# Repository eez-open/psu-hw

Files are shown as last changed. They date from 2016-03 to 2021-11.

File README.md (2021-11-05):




### Ownership and License

The contributors are listed in CONTRIB.TXT. This project uses the TAPR v1.0 license, see LICENSE.TXT.
EEZ _psu-hw_ uses the [C4.1 (Collective Code Construction Contract)](http://rfc.zeromq.org/spec:22) process for contributions.
To report an issue, use the [EEZ psu-hw issue tracker](https://github.com/eez-open/psu-hw/issues).

### Repository structure

Files in this repository are organized using the following folders:

- [Consolidated](https://github.com/eez-open/psu-hw/tree/master/Consolidated) - contains information about all modules. That include **schematics** and **PCB layout** (Eagle, .png, PDF), **BOM** (.ods, PDF) with parts required to build complete dual channel unit (1 x Aux, 2 x Power, and 1 x Arduino Shield).
*Use this as a primary reference for PCB manufacturing and assembling.*
- Aux power - information about Auxiliary power module only
- Power board - information about Power board only
- Arduino shield - information about Arduino Shield only
- [Mechanical](https://github.com/eez-open/psu-hw/tree/master/Mechanical) - drawings for metal custom enclosure and acrylic demonstration enclosure.
- [Building instructions](https://github.com/eez-open/psu-hw/tree/master/Building%20instructions) - details about power supply assembly and wire harness

### Overview

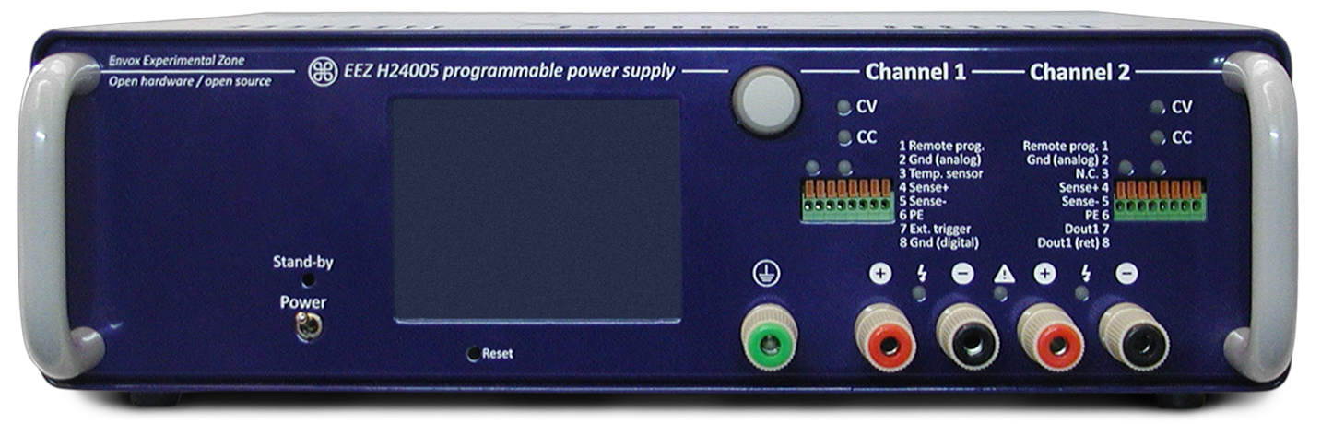
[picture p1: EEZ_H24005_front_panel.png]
prototype


This is repository for the hardware part of the DIY fully programmable dual channel bench power supply. The power supply is designed with taking into consideration the following features and requirements:

- Modular design that allows combining modules with various performance and capability and creation of multiple output solution (min. two channels)
- Voltage regulation (CV), 1/10 mV resolution, up to 50 V (default: 0 - 40 V)
- Current regulation (CC), 0.1/1 mA resolution (multiple ranges, default: 0 - 500 mA / 0 - 5 A)
- Minimal overshoot when new voltage or current level is programmed or in marginal cases such as power on/off
- 15-bit data acquisition resolution
- Various protection mechanisms: over-voltage (OVP), over-current (OCP), over-power (OPP) and over-temperature (OTP), current limiting when temperature sensors or cooling fan fault is detected
- SMPS pre-regulator circuit for lower power dissipation (using e.g. SMPS)
- SMPS pre-regulator's "100% Duty cycle" mode of operation to lower output ripple and noise 
- Switching frequency synchronization if multiple SMPS are utilized
- Output enable (OE) circuit
- Remote voltage sense
- Remote voltage programming
- External digital trigger (3.3 or 5 V logic level)
- Simple AC input protection (surge and transient protection)
- Selectable 115/230 VAC with solid-state (not mechanical!) soft-start/standby circuit
- Simple DC output protection (reverse voltage, over-voltage)
- Serial and parallel connection of the multiple channels
- MCU based digital control module using 32-bit ARM Arduino [Due](https://www.arduino.cc/en/Main/ArduinoBoardDue)
- SPI bus for communication with peripherals
- Galvanic isolation between digital module and power channels
- Real-time clock (RTC) with supercap/batter backup
- EEPROM used as a configuration and calibration parameters storage
- SD-card as an additional storage
- USB support that can be used for remote control, as a debug console and firmware upload
- Ethernet support for remote control
- Local control using TFT touch-screen display
- Incremental encoder with tactile switch as an additional mean of setting output values
- Usage of easy to find components that could be obtain with just single order from suppliers such as Farnell element14, TMU.eu, DigiKey, Mouser, RS online, etc.
- Possibility to house at least dual channel version in affordable and compact (2U height) metallic enclosure
- Comprehensive software support that include [SCPI](https://www.envox.eu/bench-power-supply/psu-scpi-reference-manual/)  remote control, GUI configuration and monitoring and even cross platform (Windows, Linux, OS X) software simulator of the firmware functionality

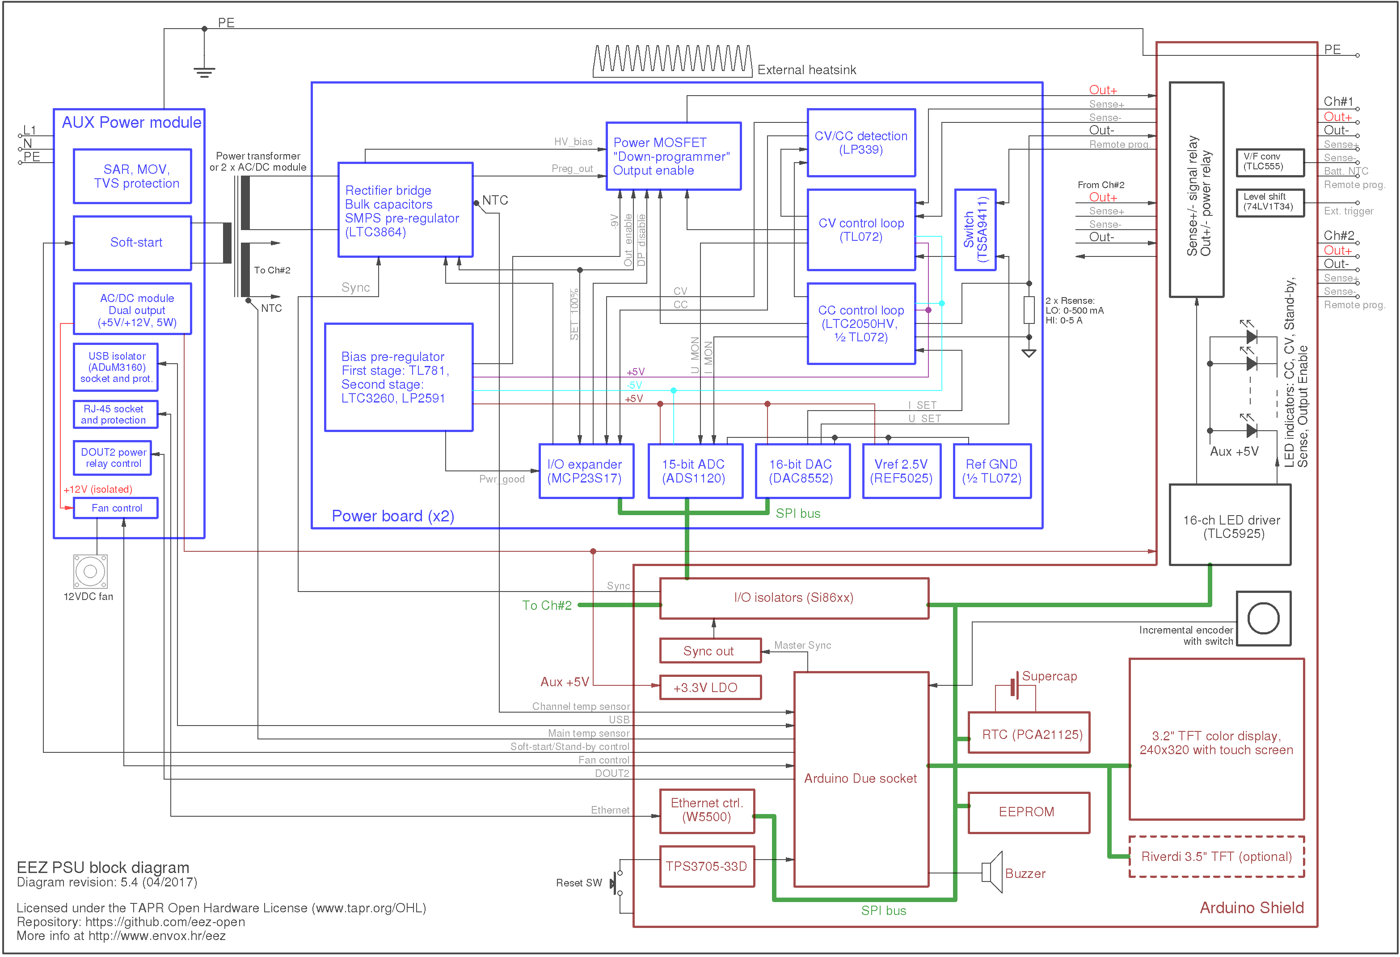
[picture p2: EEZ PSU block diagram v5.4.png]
Programmable dual channel PSU block diagram


**********************

For more information visit https://www.envox.eu/bench-power-supply/introduction/

**********************

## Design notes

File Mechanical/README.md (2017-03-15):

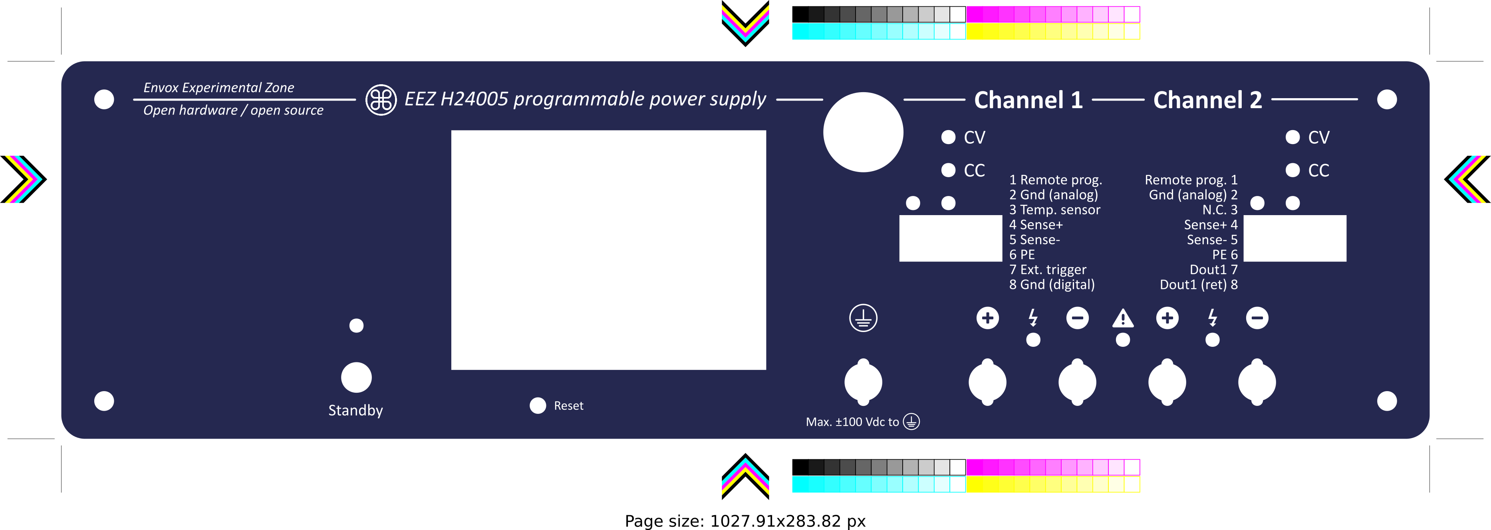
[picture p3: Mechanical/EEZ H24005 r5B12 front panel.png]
front_panel


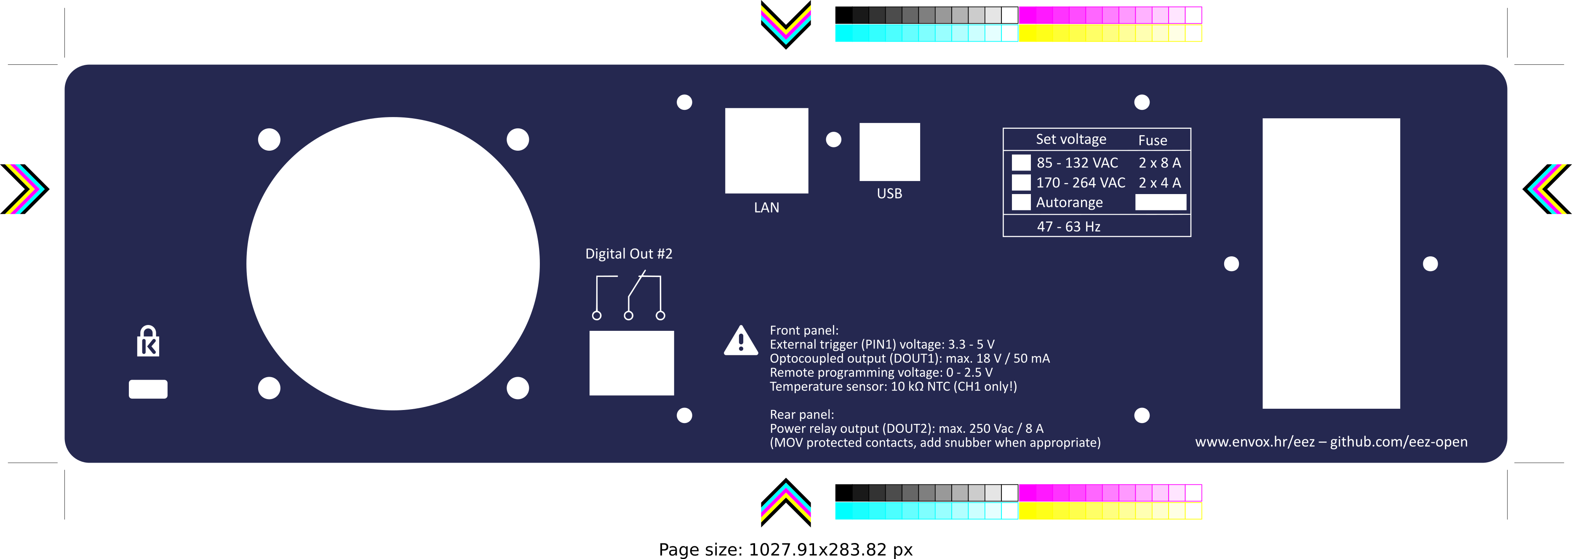
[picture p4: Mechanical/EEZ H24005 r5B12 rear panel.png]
rear_panel


* 3D model generated by [Varisom](http://www.varisom.com)
* Your can use *EEZ PSU H24005 enclosure r5B12 (for 4mm acryl).svg* for laser cut of 4mm thick acryl. The file is prepared for [Formulor](http://www.formulor.de).

**********************

Repository: www.github.com/eez-open
Web site: www.envox.hr/eez

**********************

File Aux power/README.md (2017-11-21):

Please refer to the BOM in [Consolidated/BOM](https://github.com/eez-open/psu-hw/tree/master/Consolidated/BOM) folder where **Board Name** (Col F) is *AUX PS*. Eagle files is available in [Consolidated/Eagle files](https://github.com/eez-open/psu-hw/tree/master/Consolidated/Eagle%20files) folder.

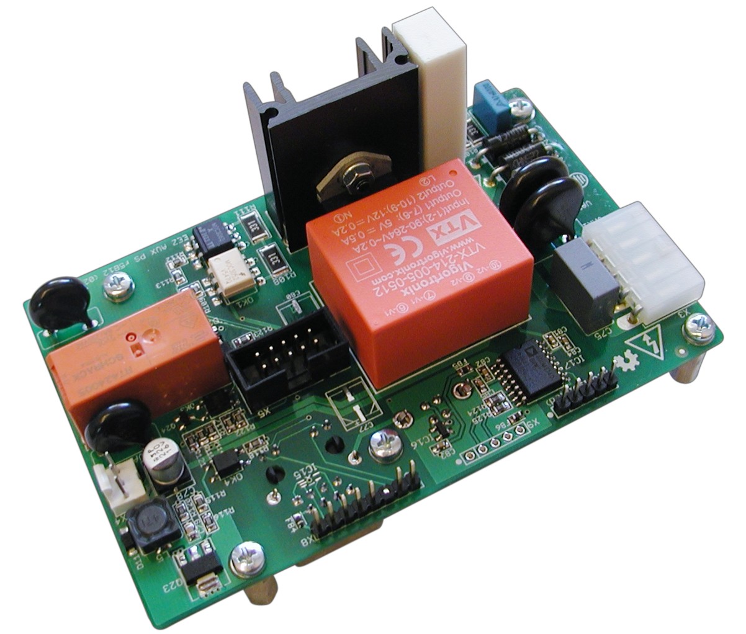
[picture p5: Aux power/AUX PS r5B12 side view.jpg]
EEZ PSU Power board r5B12


**Revision history:**
* 2017-09-24: **r5B13a**
    - USB isolator speed selection ([#56](https://github.com/eez-open/psu-hw/issues/56))
* 2017-03-24: **r5B12a**
    - Fan generates EMI, isolated fan supply, +5 V SMPS replaced with AC/DC module ([#9](https://github.com/eez-open/psu-hw/issues/9))
    - Power relay MCU controlled ([#23](https://github.com/eez-open/psu-hw/issues/23))
    - Ethernet LEDs connected wrong ([#28](https://github.com/eez-open/psu-hw/issues/28))
    - RJ45 modular jack replacement ([#34](https://github.com/eez-open/psu-hw/issues/34))
* 2017-01-11: **r5B11**
    - Added capacitor between ground and Earth ([#17](https://github.com/eez-open/psu-hw/issues/17))
* 2016-10-24: **r5B10**
    - Side 2 of USB isolator (IC19) has now power connected ([#4](https://github.com/eez-open/psu-hw/issues/4))
    - Removed +Vcc (pin 1) on USB header X9 ([#10](https://github.com/eez-open/psu-hw/issues/10))
* 2016-07-24: **r5B9** ([Version 2.0](https://github.com/eez-open/psu-hw/releases/tag/2.0) on github)
	- Replaced PCB iron core transformer with AC/DC module 12 V/5 W that support 115 / 230 VAC power input (bridge rectifier, filter capacitor and 12 V LDO for fan is not needed any more)
	- Changed Ethernet RJ-45 connector model and pinouts (X7)
	- Changed power input connector type (X4)
	- Added triac pull-down resistors R110, R111
	- Optimized number of parts size and values, renumbered reference designators
* 2016-06-14: **r5B8**
    - Master sync and power connector merged into one 10-pin IDC
    - Added place for optional USB isolator ADuM3160
    - Fixed fan control (added C97 and D21)
    - New numbering in sync with consolidated schematics
* 2016-05-26: **r4B43** ([Version 1.0](https://github.com/eez-open/psu-hw/releases/tag/1.0) on github)
	- Correction of swapping pins introduced in r4B40
* 2016-05-01: **r4B42**
    - Changed ramp capacitor from 820p to 1n
    - Fan LDO replaced with MC7812
* 2016-04-06: **r4B41**
    - Add fan control
    - Change power connector
* 2016-01-27: **r4B40**
    - A1 and A2 pins swap on triac Q1 and Q2 to lower required gate current    
    - Change KK1 heatsink type
* 2015-11-14: **r4B39** - *First public release*

**********************

This product is made available under the terms of the TAPR Open Hardware License. See the LICENSE.TXT file that accompanies this distribution for the full text of the license.

**********************

Repository: [www.github.com/eez-open](https://www.github.com/eez-open)  
Web site: [www.envox.hr/eez](https://www.envox.hr/eez)

**********************

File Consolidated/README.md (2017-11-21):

This folder contains consolidated [Eagle](https://github.com/eez-open/psu-hw/tree/master/Consolidated/Eagle%20files) and [Gerber](https://github.com/eez-open/psu-hw/tree/master/Consolidated/Gerber%20files%20%28panel%29) files of all required EEZ PSU modules:
 * Power module **r5B13** (two per unit)
 * Auxiliary power supply **r5B13a**
 * Arduino shield **r5B13a** (digital control)

Centroid files was generated using Eagle's *mount-marks-smd.ulp* script.

All components are renumbered that single BOM can be used. PCB panel is created with four boards to decrease setup fee of PCB manufacturing and assembling.

NOTE: Files for **r5B12** that is used for Crowd Supply crowdfunding campaign can be found [here](https://github.com/eez-open/psu-hw/releases/tag/3.0).

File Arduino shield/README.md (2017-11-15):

Please refer to the BOM in [Consolidated/BOM](https://github.com/eez-open/psu-hw/tree/master/Consolidated/BOM) folder where **Board Name** (Col F) is *Arduino shield*. Eagle files is available in [Consolidated/Eagle files](https://github.com/eez-open/psu-hw/tree/master/Consolidated/Eagle%20files) folder.
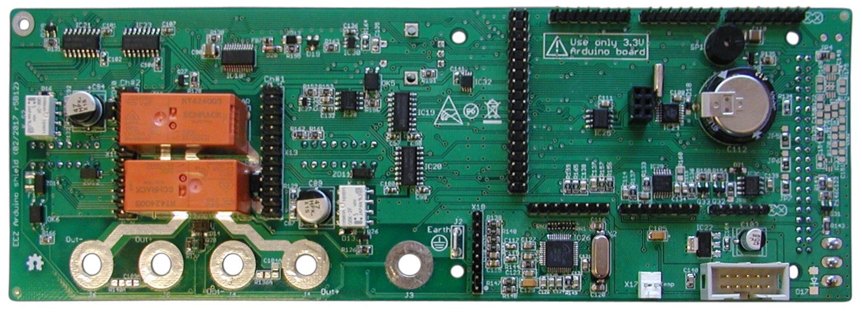
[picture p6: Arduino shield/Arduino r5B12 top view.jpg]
Shield_top

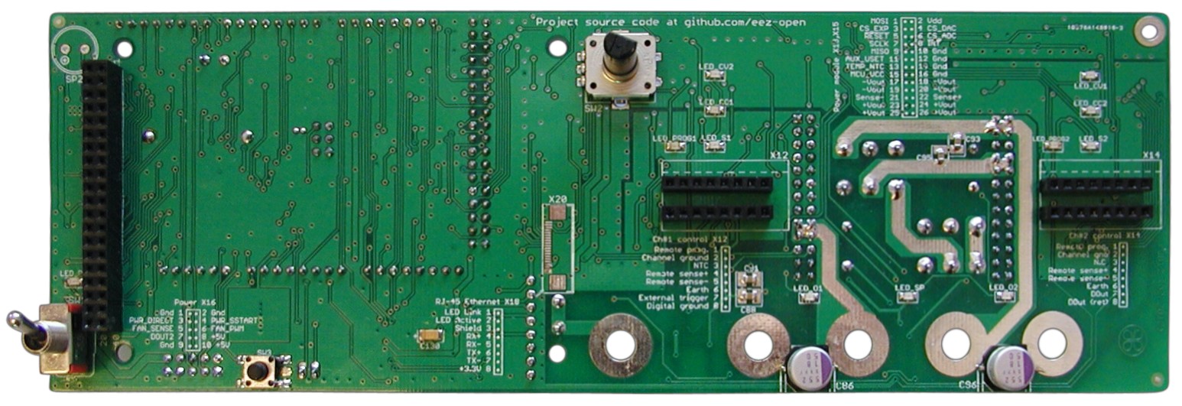
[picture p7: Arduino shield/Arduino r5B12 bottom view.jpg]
Shield_bottom


**Revision history:**
* 2017-11-04: **r5B13a**
    - Soft start and DOUT2 controls ([#36](https://github.com/eez-open/psu-hw/issues/36))
    - Removed JP5, JP6, JP7 ([#59](https://github.com/eez-open/psu-hw/issues/59))
    - R93 PCB layout spacing ([#60](https://github.com/eez-open/psu-hw/issues/60))
* 2017-09-24: **r5B12**
    - X12, X14 connection improvement on PCB ([#43](https://github.com/eez-open/psu-hw/issues/43))
* 2017-02-23: **r5B12**
    - Encoder with switch mounted directly on the PCB ([#20](https://github.com/eez-open/psu-hw/issues/20))
    - Power relay MCU controlled on the AUX PS module([#23](https://github.com/eez-open/psu-hw/issues/23))
    - Support for 3.5" Riverdi TFT touchscreen display ([#24](https://github.com/eez-open/psu-hw/issues/24))
    - Micro SD card socket ([#30](https://github.com/eez-open/psu-hw/issues/30))
* 2017-01-11: **r4B2**
    - +3.3V for buzzer ([#16](https://github.com/eez-open/psu-hw/issues/16))
    - Reorganized capacitors ([#17](https://github.com/eez-open/psu-hw/issues/17))
    - Wrong positions of DOUT pins on X14 push-in connector ([#18](https://github.com/eez-open/psu-hw/issues/18))
* 2016-12-11: **r4B1**
    - Added isolated output on X14 that is replaced with 8 pin push-in connector ([#8](https://github.com/eez-open/psu-hw/issues/8))
    - D33 is added to isolate RESET signal ([#14](https://github.com/eez-open/psu-hw/issues/14))
    - Space for optional R33 is added and IC31 is replaced with 4 AND gate ([#15](https://github.com/eez-open/psu-hw/issues/15))
* 2016-10-24: **r3B5**
    - Small adjustment of TFT display (holes and offset)
    - Removed header for optional WiFi module
    - Ethernet header (X18) is moved to the right ([#5](https://github.com/eez-open/psu-hw/issues/5))
    - Fixed wrong silkscreen for all red LEDs ([#6](https://github.com/eez-open/psu-hw/issues/6))
    - Arduino output is used to generate master sync for switching regulators ([#7](https://github.com/eez-open/psu-hw/issues/7))
    - Additional Cout is added ([#12](https://github.com/eez-open/psu-hw/issues/12))
* 2016-07-23: **r3B4** ([Version 2.0](https://github.com/eez-open/psu-hw/releases/tag/2.0) on github)
	- Corrected WATCHDOG functionality, added possibility to choose between RESET and Power off if MCU stalled
	- Optimized number of parts size and values, renumbered reference designators
* 2016-06-14: **r3B3**
    - Removed suport for Mega2560 - only 3.3 V board such as Due (and hopefully soon [STAR - OTTO](http://www.arduino.org/products/boards/arduino-star-otto) is supported
    - TFT touch screen rotated (landscape view) for housing in more compact (2U height) enclosure. Tested with both SSD1289 and ILI9341 display controllers
    - Reset supervisor and watchdog (TPS3705-33)
    - Power connector replaced with 10-pin IDC to carry master sync out
    - W5500 Ethernet controller
    - 10-pin IDC for channel's SPI bus replaced with 26-pin IDC that carry output power signals, remote sense, remote programming, temperature sensor and SMPS sync
    - Redesigned wiring of output serial/parallel connection
    - Ethernet RJ-45 connector replaced with 8-pin 0.1" header (see also new AUX PS board)
    - 2x5-pin 0.1" header for optional W5500 Ethernet module (eBay)
    - 2x4-pin 0.1" header for optional NRF24L01 Wifi module (eBay)
    - Added support for incremental encoder
    - 4 mm binding posts for remote sensing inputs replaced with 0.1" push-in connector
    - New numbering in sync with consolidated schematics
* 2016-04-06: **r1B14** ([Version 1.0](https://github.com/eez-open/psu-hw/releases/tag/1.0) on github)
    - Added fan control (FAN_PWM, FAN_SENSE)
    - Power connector replaced with 6-pin IDC as on the AUX PS r4B41
    - Removed optional reset connector
* 2016-03-28: **r1B13a**
    - Change remote sense inputs position on X4
* 2016-03-27: **r1B13**
    - Fixed remote sense wiring
    - Output protection redesigned (TVS moved, SAR and MOVs removed)
    - Smaller footprint
    - Remote sense 4 mm banana binding posts replaced with compact "push-in" connectors
    - Digital trigger input (with buffer and level shifter) added
    - THT LEDs replaced with SMD counterparts (lightpipes are now required)
* 2015-12-07: **r1B12b** - *First public release*

**********************

This product is made available under the terms of the TAPR Open Hardware License. See the LICENSE.TXT file that accompanies this distribution for the full text of the license.

**********************

Repository: [www.github.com/eez-open](https://www.github.com/eez-open)  
Web site: [www.envox.hr/eez](https://www.envox.hr/eez)

**********************

Consult [EEZ PSU Arduino pin mapping r5B12.odt
](https://github.com/eez-open/psu-hw/raw/master/Arduino%20shield/EEZ%20PSU%20Arduino%20pin%20mapping%20r5B12.odt) for Arduino pins assignements and [EEZ PSU Arduino shield+BP TLC5925 codes r3B3.odt](https://github.com/eez-open/psu-hw/raw/master/Arduino%20shield/EEZ%20PSU%20Arduino%20shield%2BBP%20TLC5925%20codes%20r3B3.odt) for binding posts connections and LED indications.

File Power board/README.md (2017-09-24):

Please refer to the BOM in [Consolidated/BOM](https://github.com/eez-open/psu-hw/tree/master/Consolidated/BOM) folder where **Board Name** (Col F) is *Power board*. Eagle files is available in [Consolidated/Eagle files](https://github.com/eez-open/psu-hw/tree/master/Consolidated/Eagle%20files) folder.

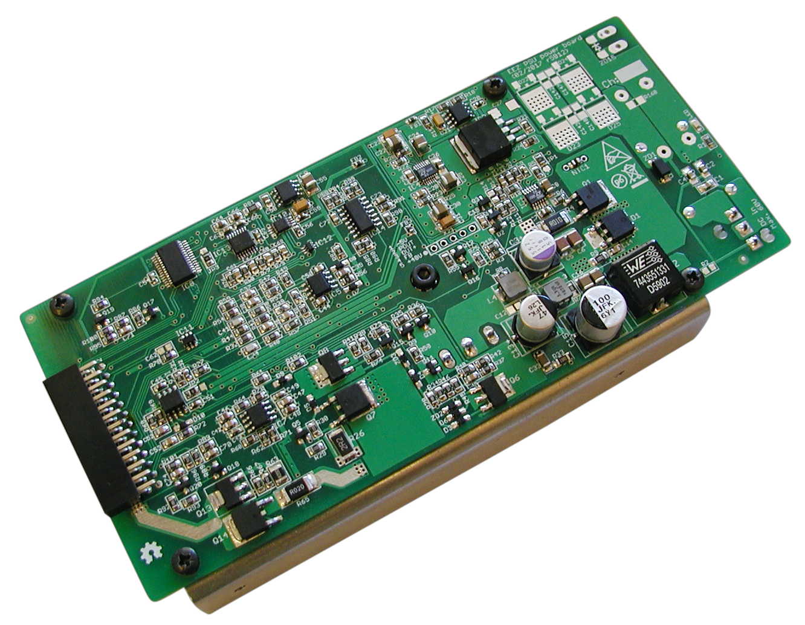
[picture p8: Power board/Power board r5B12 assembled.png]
r5b12


**Revision history:**
* 2017-09-24: **r5B13**
    - High range (0-5 A) sense resistor improvement ([#40](https://github.com/eez-open/psu-hw/issues/40))
    - Additional current range 0-50 mA ([#41](https://github.com/eez-open/psu-hw/issues/41))
    - Output enters unregulated mode too early ([#42](https://github.com/eez-open/psu-hw/issues/42))
    - Remote sense resistors removed ([#44](https://github.com/eez-open/psu-hw/issues/44))
    - Overvoltage protection for V+ output ([#46](https://github.com/eez-open/psu-hw/issues/46))
* 2017-03-11: **r5B12**
    - Dual range current programming and measurement (0-500 mA, 0-5 A)
    - New current monitor (LTC3050HV)
    - 16-bit I/O expander
    - New bias pre-regulator (TL783, LTC3260)
    - Additional Vin capacitor on Power board ([#19](https://github.com/eez-open/psu-hw/issues/19))
    - Rsense with 4-terminal sensing ([#21](https://github.com/eez-open/psu-hw/issues/21))
    - Protection improvement for DC power input ([#25](https://github.com/eez-open/psu-hw/issues/25))
    - PCB is now 15 mm longer (but still compatible with previous heatsink/mounting holes)
* 2016-12-11: **r5B11**
	- Current limiter is removed
* 2016-10-24: **r5B10**
	- Added optional components on the AC power input
	- Voltage programming switch (IC13) wiring is fixed ([#2](https://github.com/eez-open/psu-hw/issues/2))
	- Main heatsink (Q4) earth connection is removed ([#3](https://github.com/eez-open/psu-hw/issues/3))
	- Error amps ground reference offset ([#11](https://github.com/eez-open/psu-hw/issues/11))
* 2016-07-23: **r5B9** ([Version 2.0](https://github.com/eez-open/psu-hw/releases/tag/2.0) on github)
	- DAC Vdd input moved from digital +5 V to analog +5 V power supply
	- Changed power input connector type (X1)
	- Optimized number of parts size and values, renumbered reference designators
* 2016-06-16: **r5B8** - first public release (successor of pre- and post-regulator boards available in [Version 1.0](https://github.com/eez-open/psu-hw/releases/tag/1.0) on GitHub)
	- SMPS pre-regulator based on LTC3864
	- 100% duty-cycle mode of operation for lower output ripple
	- Choice between AC and DC power input
	- Remote output voltage programming
	- Remote sense reverse polarity protection
	- Switching frequency synchronization with other channel via Arduino Shield board (no additional cable is required)
	- On-board SMT temperature sensor (no additional cable is required)

This product is made available under the terms of the TAPR Open Hardware License. See the LICENSE.TXT file that accompanies this distribution for the full text of the license.

**********************

Repository: [www.github.com/eez-open](https://www.github.com/eez-open)  
Web site: [www.envox.hr/eez](https://www.envox.hr/eez)

**********************

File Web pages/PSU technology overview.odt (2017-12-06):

# Technology overview

This programmable bench power supply (PSU) was designed taking into consideration the following mixture of goals and requirements:

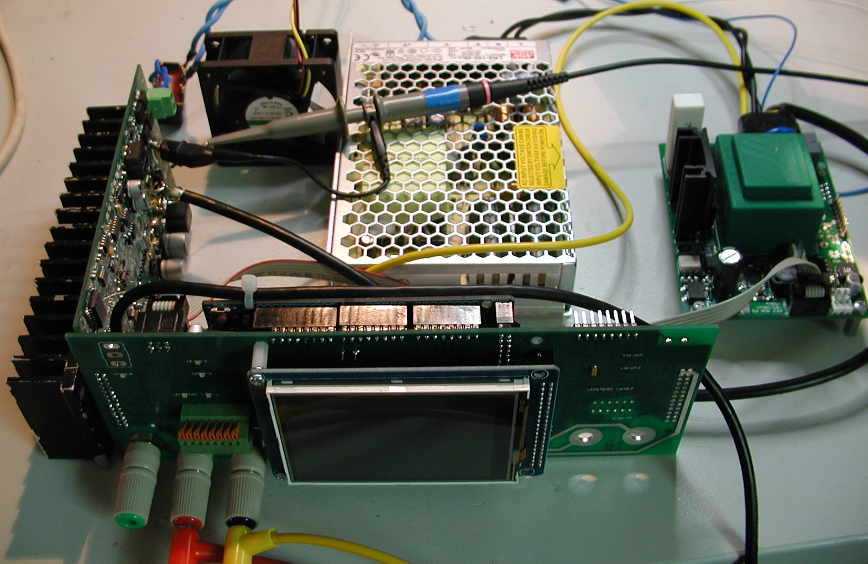
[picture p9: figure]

(http://www.envox.hr/eez/images/eez_psu_prototype_r5b6.jpg)Fig. 1: EEZ PSU early prototype

- Modular design allowing a combination of modules with various performance and capability and creation of multiple output solution (e.g. a minimum of two channels)
- A single input for both internal power and bias supplies, removing any need for a custom multiple secondary winding main transformer
- SMPS (switch mode power supply) pre-regulator circuit for lower power dissipation
- SMPS pre-regulator "100% Duty cycle" operational mode to reduce ripple and noise on the PSU's output
- A TFT color touch-screen as an input control device, and a display output for perfomance information
- Microcontroller (MCU) managed serial and parallel connection for combining PSU channel outputs if suitable
- Voltage limit regulation (CV) with 1/10 mV resolution, up to 50 V (default: 0 – 40 V)
- Current limit regulation (CC) with 0.1/1 mA resolution (when dual range operation, default: 0 – 500 mA / 0 – 5 A)
- Minimal overshoot when a new voltage or current level is programmed, or for cases at the margin, such as power on/off
- A minimum of 15-bit resolution for data acquisition for controlling the PSU
- Multiple protection mechanisms, for both the PSU itself and for devices it powers: over-voltage (OVP), over-current (OCP), over-power (OPP), over-temperature (OTP), and automatic current limiting when faults in temperature sensors or the cooling fan are detected
- Switching frequency synchronization (http://www.powerguru.org/synchronization-of-smps-power-modules/) between switching regulators
- Output enable (OE) circuit, allowing instant (as nearly as possible) output disconnection
- Remote voltage sensing, i.e. Kelvin wiring
- Remote voltage programming (external) “analog” signal control
- External digital trigger signal (3.3 or 5 V logic level)
- Conventional AC input protection for the entire PSU (surge and transient protection)
- Selectable 115/230 VAC with solid-state (not mechanical!) soft-start/standby circuit
- Simple DC output protection (reverse voltage, over-voltage)
- Serial and parallel, firmware controlled, connection of two power output channels
- An MCU based digital control module using 32-bit Arduino/Genuino boards such as the Due (https://www.arduino.cc/en/Main/ArduinoBoardDue)
- An SPI bus (https://en.wikipedia.org/wiki/Serial_Peripheral_Interface_Bus) for peripheral communication
- Galvanic isolation (https://en.wikipedia.org/wiki/Galvanic_isolation) between the digital control circuitry and the power channels
- A real-time clock (RTC) with supercap/battery backup
- An EEPROM for configuration and calibration parameter storage
- Provisions for an SD-card as an additional storage
- USB support for remote control, as a debug console, and for firmware upload
- Ethernet support for remote control
- Fan speed control to reduce operational noise
- An incremental encoder with tactile switch as an additional means of setting output values
- Use of easy to find components readily available from suppliers such as Farnell element14, TMU.eu, DigiKey, Mouser, RS online, etc.
- Possibility to house at least two channels in an affordable and compact (2U height) metallic enclosure
- Comprehensive software support including SCPI remote control, GUI configuration and monitoring, and even a cross platform (Windows, Linux, OS X) PSU function software simulator

Despite the complexity of the proposed design, it should easily possible for DIY assembly needing only intermediate soldering skills for SMD components. The PCB (both Eagle and Gerber files) for PCB production are available on GitHub (https://github.com/eez-open/psu-hw). Arrangements have been made to offer PCBs directly from suppliers, e.g. OSHpark (https://oshpark.com/profiles/eez-open).

Upload of revised firmware will require only novice programming skills and some familiarity with the Arduino IDE. Short video (https://www.youtube.com/watch?v=1iFb0VypKnE) illustrating download and installation of firmware revisons have been made available.

## The PSU building blocks and default configuration

The power supply’s modular design allows freedom to build a flexible, and functional, device. The following modules is possible to use for PSU building:

- Auxiliary power module (http://www.envox.hr/eez/bench-power-supply/psu-auxiliary-supply.html),
- Power board (http://www.envox.hr/eez/bench-power-supply/power-board.html) (one per channel), and
- Arduino Shield (digital control) (http://www.envox.hr/eez/bench-power-supply/psu-digital-control.html)

Each module is described in more detail below. The default configuration has been named EEZ H24005, and will come with the following features:

- Two “floating” channel with programmable output voltage range 0 – 40 V and current 0 – 5 A (max. 155 W per channel) or 0 – 80 V and 0 – 10 A with MCU managed connection in series or parallel
- Remote voltage sensing (with inverse polarity protection), remote voltage programming
- External digital trigger input, external temperature sensor
- Temperature controlled cooling fan
- AC mains power supplied to two AC/DC power modules (48 Vdc, 155 W)
- Arduino Due based digital control
- 3.2” TFT color touch-screen for local console and operating condition display
- Ethernet and USB for remote control (USB is used for firmware update)
- Metal enclosure: 80 (H) x 290 (W) x 240 (D without handles) mm

## Functional block diagram

The block diagram of the PSU is shown below. It includes four modules. The auxiliary power module is used, among other things, for autonomous power of the Arduino Shield board. Complete control of all functionality is performed using the local TFT display touch screen. In addition, the Arduino Shield enables fully featured remote control using serial (via USB) or Ethernet communication.

The remote control is based on a command set that complies with the SCPI (https://en.wikipedia.org/wiki/Standard_Commands_for_Programmable_Instruments) 1999.0 (http://www.ivifoundation.org/specifications/default.aspx) specification which is the de facto standard for middle and high-end commercial power supplies, and many other laboratory instruments.

## Module description


(http://www.envox.hr/eez/images/eez_psu_block_diagram_5_4.png)Fig. 2: EEZ PSU functional block diagram

More information about modules used for building the PSU can be found in the following chapters. A header section with information about module development status has been added to each chapter to simplify progress tracking, like:

Current version | r4B39
Status | Completed, ready for production
PCB manufactured | Yes
PCB assembled | Yes
BOM (https://en.wikipedia.org/wiki/Bill_of_materials) | Yes (Farnell, TME)
File repository | https://github.com/eez-open/psu-hw/tree/master/Aux%20power

## Schematics

{jd_file file==17}

{jd_file file==15}

Revision: 0.2 (of 3) Last modified: 2017-05-10

Revision: 0.2 1 (of 3) Last modified: 2017-05-10

DRAFT – PSU technology overview

Last modified: 2017-05-10 2 (of 3) Doc. version: 0.2

Revision: 0.2 3 (of 3) Last modified: 2017-05-10

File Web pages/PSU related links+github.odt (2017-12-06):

EEZ PSU on the EEVblog forum (http://www.eevblog.com/forum/projects/diy-programmable-dual-channel-bench-psu-0-50v3a/)

EEZ PSU on the DIYaudio forum (http://www.diyaudio.com/forums/equipment-tools/268220-diy-programmable-dual-channel-bench-psu-0-50v-3a.html)

EEZ PSU on the YU3MA.net forum (http://forum.yu3ma.net/showthread.php?tid=980)

EEZ PSU on the Hackaday.io (https://hackaday.io/project/9491-diy-programmable-scpi-bench-power-supply)

EEZ PSU on the Hackster.io (https://www.hackster.io/prasimix/diy-programmable-scpi-bench-power-supply-5e59d5)

Hackaday (https://hackaday.com/2016/02/06/build-yourself-an-awesome-modular-power-supply/) about EEZ PSU (thanks Elliot!)

## DIY power supply projects

We are trying here to make a collection of open source power supplies. Please find below what we found so far (sorted alphabetically) and you are welcome with your suggestions.

Only a project that include some sort of programming and is open source will be listed.

Circuitmaker (http://circuitmaker.com/Projects/F48BC6C2-9005-48B8-87CD-C89CD40F70DC) | Danger From Deer – Bench power supply build (https://dangerfromdeer.com/2016/01/01/bench-power-supply-build-part-1/)
| DIYaudio forum – Frex: Triple outputs 160W Lab PSU – EPSUX3 version 2 (http://www.diyaudio.com/forums/equipment-tools/263471-triple-outputs-160w-lab-psu-epsux3-version-2-a.html)
| EEVblog – μSupply (http://www.eevblog.com/projects/usupply/), a compact Arduino compatible battery powered laboratory power supply
| EEVblog forum – Cowana: Korad KA3003D redesign and upgrade (http://www.eevblog.com/forum/projects/korad-ka3003d-redesign-and-upgrade/)
| EEVblog forum (Leonid Ivanovitch) – PSL-3604 DIY Bench Power Supply (http://www.eevblog.com/forum/projects/diy-bench-power-supply-psl-3604/msg622093/#msg622093)
| Elektor Magazine – Sunil_M: Platino Adjustable Bench Power Supply (https://www.elektormagazine.com/labs/platino-adjustable-bench-power-supply-130406-1)
| Gerrysweeney.com – Fully Programmable Modular Bench Power Supply (http://gerrysweeney.com/fully-programmable-modular-bench-power-supply/)
GitHub (https://github.com/g4lvanix/elbsupply) | Hackaday.io – ElbSupply: Simple linear bench supply (https://hackaday.io/project/4407-elbsupply-simple-linear-bench-supply)
GitHub (https://github.com/fridrikfreyr/DPS201-Hardware) | Hackaday.io – Fridrik: DPS201 Lab PSU (https://hackaday.io/project/1948-dps201-lab-psu)
| Ian Johnston.com – Project #021, Home Built Bench Power Supply (http://www.ianjohnston.com/index.php/projects/57-project-021-home-built-bench-power-supply)
| Kerry Wong – A Digitally Controlled Dual Tracking Power Supply (http://www.kerrywong.com/2013/11/24/a-digitally-controlled-dual-tracking-power-supply-i/)
| Koyodza – Bench lab power supply PSA2 (http://www.koyodza.com/PSA2/index.php?lng=EN)
GitHub (https://github.com/tom-biskupic/LabPSU) | Musings of a WAHZ – Lab Power Supply (http://wahz.blogspot.com.au/p/lab-power-supply.html)
GitHub (https://github.com/qwertyboy/power-supply) | Quertyboy design – Digital PSU (https://qwertyboydesign.wordpress.com/projects-2/digital-psu/)
GitHub (https://github.com/semianalog/mod12003) | Semianalog.com – MOD1 modular power supply (https://github.com/semianalog/mod12003)
GitHub (https://github.com/ThomasVDD/SmartSupply) | ThomasVDD – SmartSupply (http://www.instructables.com/id/Digital-Battery-Operated-Powersupply/) (Digital Battery Operated Power supply)
| Tuxgraphics.org – A Digital DC Power Supply (http://tuxgraphics.org/electronics/201005/bench-power-supply-v3.shtml) (programmable bench power supply unit), hardware version 3.0

## Other

List of open source “ingredients” that could be used as building blocks for DIY power supplies.

GitHub (https://github.com/yu3ma/FSFR2100_LLC_SMPS) | Yu3ma – LLC resonant half-bridge isolated 200W Switched Mode Power Supply based on Fairchild's (now On Semiconductors) FSFR2100XS power controller.
| Iowa Scaled Enginnering – Rebuilding the Elektor 400W power supply: pre-regulator (http://www.iascaled.com/rebuilding-the-elektor-400w-power-supply-pre-regulator/)

DRAFT – PSU related links+github

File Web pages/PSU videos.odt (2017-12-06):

# Videos

<iframe width="320" height="200" src="https://www.youtube.com/embed/jofIdGx2gTg" frameborder="0" allowfullscreen></iframe> | | First preview of the M2 firmware where various input methods are implemented. Thanks to that touch screen become a valid substitute for potentiometer, incremental encoder or numeric keypad. In total five more of operation is possible: Slider (interactive and non-interactive), Step (interactive and non-interactive) and Keypad (non-interactive)
<iframe width="320" height="200" src="https://www.youtube.com/embed/1iFb0VypKnE" frameborder="0" allowfullscreen></iframe> | | The EEZ power supply is using Arduino for programming and monitoring. Therefore its firmware can be partially tested when uploaded on Mega2560 or Due board without having power supply completed. This video contains required steps for upload to the Mega board and test remote control capability based on SCPI commands.
<iframe width="320" height="200" src="https://www.youtube.com/embed/hhGT8GlrUEk" frameborder="0" allowfullscreen></iframe> | | EEZ PSU firmware can be run and evaluate even without having real device on hand. We are developed software simulator that can be run on all major platforms and can be used for presentations but also for development.
<iframe width="320" height="200" src="https://www.youtube.com/embed/b-SwEfrz-Qk" frameborder="0" allowfullscreen></iframe> | | Firmware M2 in addition to the SCPI remote control comes with support for local control via TFT color touchscreen display. This video shows what functionality is covered in this release candidate version.
<iframe width="320" height="200" src="https://www.youtube.com/embed/mfQvZW9PMwk" frameborder="0" allowfullscreen></iframe> | | The EEZ PSU H24005 channel’s output values can be presented in three different ways: Digits Horizontal bar graph Vertical bar graph
<iframe width="320" height="200" src="https://www.youtube.com/embed/s_yasI__Yoo" frameborder="0" allowfullscreen></iframe> | | EEZ PSU H24005 protection mechanisms: Power-on self test Power channel failure Temperature sensor failure Fan failure Over-current protection (OCP) Over-voltage protection (OVP) Over-power protection (OPP) Over-temperature protection (OTP) Remote sense reverse polarity protection
<iframe width="320" height="200" src="https://www.youtube.com/embed/Wbq7mmp_3rc" frameborder="0" allowfullscreen></iframe> | | EEZ PSU H24005 voltage and current calibration using Calibration wizard
<iframe width="320" height="200" src="https://www.youtube.com/embed/wzr1Q3uVOPo" frameborder="0" allowfullscreen></iframe> | | EEZ PSU H24005 remote control using SCPI commands send via serial (USB) or Ethernet. Establishing connection with SCPI controller application (Keysight Connection Expert) is also demonstrated.
<iframe width="320" height="200" src="https://www.youtube.com/embed/5BYZ7RP3CQs" frameborder="0" allowfullscreen></iframe> | | The tracking mode of operation allows one to set output values, states and protections on the both channel by programming just one of them. That could speed up programming and reduce a chance to make mistake when e.g. symmetrical output is needed (on channel is used as positive and another as negative rail) that programmed values is not equal.
<iframe width="320" height="200" src="https://www.youtube.com/embed/Ukn1K1G0pJU" frameborder="0" allowfullscreen></iframe> | | The EEZ H24005 has two isolated channels, the outputs of which can be combined to get higher voltage (up to 80 V) or current (up to 10 A), within the overall power limit of 310 W. Unlike many other power supplies that allow such channel coupling, with the EEZ H24005 you don’t need to pay special attention to wiring thanks to built-in power relays for both voltage and current coupling. This decreases the risk of damaging the power supply due to a tiny wiring mistake.
<iframe width="320" height="200" src="https://www.youtube.com/embed/GRbDXmmBcUA" frameborder="0" allowfullscreen></iframe> | | Presentation of the following system protection mechanisms: Disabling outputs when Auto-recall user profile option is selected Shutdown when any of protection tripped Switching off all outputs when any of protection tripped Disable all outputs on start up
<iframe width="320" height="200" src="https://www.youtube.com/embed/_bRxJo1zC8U" frameborder="0" allowfullscreen></iframe> | | See how to use external analog signal for controlling voltage output.
<iframe width="320" height="200" src="https://www.youtube.com/embed/tPuPrHchPfc" frameborder="0" allowfullscreen></iframe> | | YT mode allows one to directly monitor on the TFT display what is happening over a long period of time with output voltage, current, or power without the assistance of a PC or other external device.
<iframe width="320" height="200" src="https://www.youtube.com/embed/12qwjicYb90" frameborder="0" allowfullscreen></iframe> | | First preview of added incremental encoder that can be used for selecting and setting output values.
<iframe width="320" height="200" src="https://www.youtube.com/embed/1OuaQSNv5TA" frameborder="0" allowfullscreen></iframe> | | Remote voltage sensing can be used to delivery exact voltage to the load regardless of the voltage drop on the connecting cables caused by current flow.
<iframe width="320" height="200" src="https://www.youtube.com/embed/gfUSl8hXwjE" frameborder="0" allowfullscreen></iframe> | | First preview of EEZ Studio, a visual toolkit we developed and used for the EEZ H24005 to create the TFT touch-screen display GUI.
<iframe width="320" height="200" src="https://www.youtube.com/embed/hv_wY3ePyhI" frameborder="0" allowfullscreen></iframe> | | Trigger system and list programming – Part 1 of 2 shows how is possible to trigger a change of output values using one of four trigger sources.
<iframe width="320" height="200" src="https://www.youtube.com/embed/yGn3uoRkYyg" frameborder="0" allowfullscreen></iframe> | | Trigger system and list programming – Part 2 of 2 shows how is possible to program outputs using list of up to 256 different voltage and current values.
<iframe width="320" height="200" src="https://www.youtube.com/embed/wG9moiu5fOY" frameborder="0" allowfullscreen></iframe> | | Using of foot pedal to control outputs.

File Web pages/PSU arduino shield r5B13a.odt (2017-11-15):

# Arduino Shield (digital control)

Current version | r5B13a
Status | Completed, ready for production
PCB manufactured | Yes (r5B12)
PCB assembled | Yes (r5B12)
BOM | Yes (Farnell, TME, Digikey, Mouser, RS)
File repository | https://github.com/eez-open/psu-hw/tree/master/Arduino shield (include Eagle, Gerber and BOM files)
License | TAPR v1.0 (http://www.tapr.org/TAPR_Open_Hardware_License_v1.0.txt)
Contributions | C4.1 (Collective Code Construction Contract) (https://rfc.zeromq.org/spec:22/C4/)

Revision history

2017-11-04: r5B13a

- Improved soft start and DOUT2 controls (#36 (https://github.com/eez-open/psu-hw/issues/36))
- Removed JP5, JP6, JP7 on Arduino shield (#59 (https://github.com/eez-open/psu-hw/issues/59))
- R93 PCB layout spacing (#60 (https://github.com/eez-open/psu-hw/issues/60))

2017-09-24: r5B13

- X12, X14 connection improvement on PCB (#43 (https://github.com/eez-open/psu-hw/issues/43))

2017-02-23: r5B12 (Version 3.0 (https://github.com/eez-open/psu-hw/releases/tag/3.0) on GitHub)

- Encoder with switch mounted directly on the PCB (#20 (https://github.com/eez-open/psu-hw/issues/20))
- MCU controlled power relay on the AUX PS module(#23 (https://github.com/eez-open/psu-hw/issues/23))
- Support for 3.5" Riverdi TFT touchscreen display (#24 (https://github.com/eez-open/psu-hw/issues/24))
- Micro SD card socket (#30 (https://github.com/eez-open/psu-hw/issues/30))

2017-01-11: r4B2

- +3.3V for buzzer (#16 (https://github.com/eez-open/psu-hw/issues/16))
- Reorganized capacitors (#17 (https://github.com/eez-open/psu-hw/issues/17))
- Fixed wrong positions of DOUT pins on X14 push-in connector (#18 (https://github.com/eez-open/psu-hw/issues/18))

2016-12-11: r4B1

- Added isolated output on X14 that is replaced with 8 pin push-in connector (#8 (https://github.com/eez-open/psu-hw/issues/8))
- D33 added to isolate RESET signal (#14 (https://github.com/eez-open/psu-hw/issues/14))
- Space for optional R33 added and IC31 replaced with 4 AND gate (#15 (https://github.com/eez-open/psu-hw/issues/15))

2016-10-24: r3B5

- Small adjustment of TFT display (holes and offset)
- Removed header for optional WiFi module
- Ethernet header (X18) moved to the right (#5 (https://github.com/eez-open/psu-hw/issues/5))
- Fixed wrong silkscreen for all red LEDs (#6 (https://github.com/eez-open/psu-hw/issues/6))
- Arduino output now used to generate master sync for switching regulators (#7 (https://github.com/eez-open/psu-hw/issues/7))
- Additional Cout is added (#12 (https://github.com/eez-open/psu-hw/issues/12))

2016-07-24: r3B4 (Version 2.0 (https://github.com/eez-open/psu-hw/releases/tag/2.0) on GitHub)

- Corrected WATCHDOG functionality, added possibility to choose between RESET and Power off if MCU stalled
- Optimized number of parts size and values, renumbered reference designators

2016-06-14: r3B3

- Removed support for Mega2560 – only 3.3 V board such as Due (and hopefully soon STAR - OTTO (http://www.arduino.org/products/boards/arduino-star-otto)) now supported
- TFT touch screen rotated (landscape view) for housing in more compact (2U height) enclosure. Tested with both SSD1289 and ILI9341 display controllers
- Reset supervisor and watchdog (TPS3705-33)
- Power connector replaced with 10-pin IDC to carry master sync out
- W5500 Ethernet controller
- 10-pin IDC for channel's SPI bus replaced with 26-pin IDC which carries output power signals, remote sense, remote programming, temperature sensor and SMPS sync
- Redesigned wiring of output serial/parallel connection
- Ethernet RJ-45 connector replaced with 8-pin 0.1" header (see also new AUX PS board)
- 2x5-pin 0.1" header for optional W5500 Ethernet module (eBay, etc.)
- 2x4-pin 0.1" header for optional NRF24L01 WiFi module (eBay, etc.)
- Added support for incremental encoder
- 4 mm binding posts for remote sensing inputs replaced with 0.1" push-in connector

2016-04-06 r1B14 (Version 1.0 (https://github.com/eez-open/psu-hw/releases/tag/1.0) on github)

- Added fan control (FAN_PWM, FAN_SENSE)
- Power connector replaced with 6-pin IDC as on the AUX PS r4B41
- Removed optional reset connector

2016-03-28 r1B13a

- Changed remote sense inputs position on X4

2016-03-27 r1B13

- Fixed remote sense wiring
- Output protection redesigned (TVS moved, SAR and MOVs removed)
- Smaller footprint
- Remote sense 4 mm banana binding posts replaced with compact "push-in" connectors
- Digital trigger input (with buffer and level shifter) added
- THT LEDs replaced with SMD counterparts (lightpipes now required)

2015-12-07 r1B12b – First public release


(http://www.envox.hr/eez/images/arduino_shield_r5b12_top.jpg)Fig. 1: Arduino Shield assembled (PCB r5B12, top side)


(http://www.envox.hr/eez/images/arduino_shield_r5b12_bottom.jpg)Fig. 2: Arduino Shield assembled (PCB r5B12, bottom side)

The Arduino Shield (https://www.arduino.cc/en/Main/ArduinoShields) has three important functions:

- Carrying power output binding posts and remote sense inputs with the option to connect two output channels in series or parallel,
- MCU programming and supervision of up to two Power boards (http://www.envox.hr/eez/bench-power-supply/power-board.html) and
- Local user interface using TFT color touch-screen display

Additionally it offers the following functionality:

- Multiple LED status and operational indications
- Soft-start/Stand-by control (hosted on Auxiliary power (http://www.envox.hr/eez/bench-power-supply/psu-auxiliary-supply.html) module)
- MCU fan control (hosted on Auxiliary power (http://www.envox.hr/eez/bench-power-supply/psu-auxiliary-supply.html) module)
- EEPROM storage
- Real-time clock (RTC) with supercap (https://en.wikipedia.org/wiki/Supercapacitor) back-up
- Reset supervisor with watchdog
- Beeper
- Analog inputs for temperature readings
- Ethernet communication
- Incremental encoder with switch
- Switching regulator frequency synchronization
- External digital trigger
- Power relay (DOUT2) control (hosted on Auxiliary power (http://www.envox.hr/eez/bench-power-supply/psu-auxiliary-supply.html) module)
- Optional audio amplifier and 20-pin FFC connector for 3.5” Riverdi TFT touch-screen displays

## Binding posts section

This section has been added to simplify wiring of power binding posts, remote sense inputs, and serial and parallel connection control for the two channels without external wiring changes. Wiring of power outputs is controlled by the MCU firmware to reduce the possibility of an operator error, such as:

- channel output voltages and currents are not adjusted properly before connecting them in parallel,
- channel output polarities are mismatched or
- serial wiring is established while outputs are enabled that increase the risk of electric shock because of touching output when 50 V or more is present. An exceptionally dangerous situation since fire or electrocution is much increased at these voltages.

Output terminals have been located on the PCB so that direct mounting of 4 mm paired binding posts (with standard spacing of 19.05 mm / 750 mils) is supported. Power outputs are protected against reverse polarity and over-voltage spikes using TVS (ZD7, ZD10). Output capacitors (C87+R129, C89 and C92+R132, C94) required for both stable operation and lowered output PARD (http://power-topics.blogspot.hr/2008/11/ripple-noise-specs-and-measurements.html) (ripple and noise) of Power modules are also mounted on the Power board PCB. For additional attenuation of PARD, C86 and C96 (elco-polymer, like OS-CON) are mounted in close proximity to the power output binding posts.

Connecting two power outputs in series or parallel is done with two 8 A relays (K_SER, K_PAR). The channel outputs are separated/isolated when both relays are inactive; J1, J4 and J5, J6 binding post pairs are used for Ch1 and Ch2 respectively. When operating in either series or parallel, only two central binding posts (J4, J5) are used. This design choice was intentional to decrease the chance of bringing high voltage or current to loads already connected to either channel. In this way, the user need to physically move one or another wire to make a new operational scheme effective.

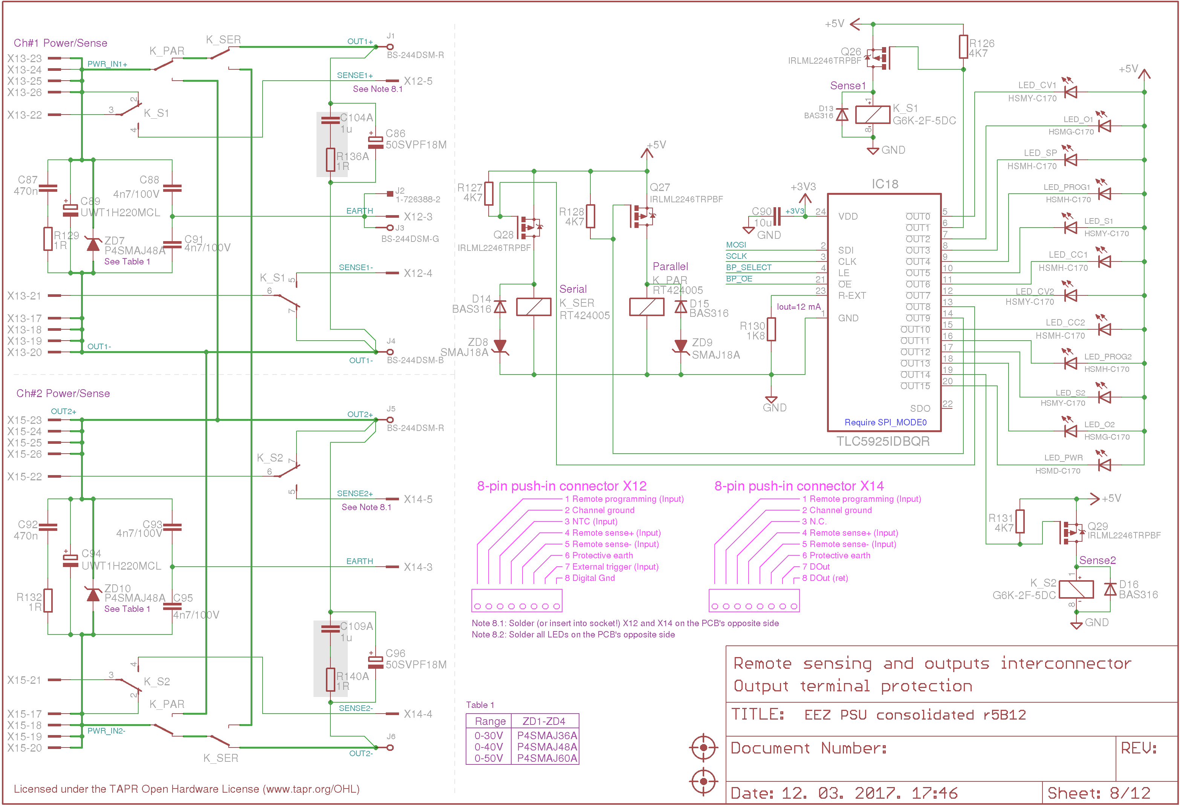
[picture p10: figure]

(http://www.envox.hr/eez/images/arduino_shield_r5b12_sheet8of12.png)Fig. 3: Binding post section, relays and LED driver

In addition, with this scheme with K_SER and K_PAR avoids the possibility of Power board damage due to a firmware bug that can activate both modes concurrently. The wiring in Fig. 4 makes clear that Parallel mode is more “significant” – when it’s selected it locks out the K_SER input contacts.

An obvious drawback of this wiring approach is disconnecting the C86, C96 capacitors when power outputs are coupled. Therefore, if lower PARD figure is still needed an external capacitor may be necessary.

When driving the serial or parallel relays, the following things have to be taken into consideration:

- Voltage and current must be zero before the channels are connected or disconnected. The easiest way to do that is to disable output (OE is off) but it's also recommended to also program output values to zero.
- Coupling outputs in parallel is safely possible if programmed output voltages are the same on both channels
- Optionally, the down-programmer circuit could be disconnected on one of the channels when coupling in parallel is selected

Of course, wiring of two channels can be done independently of their built-in functionality. In this case, the recommendations above still apply.

Channel outputs, by default, are “floating” with regard to the PSU earth potential provided via a separate 4 mm binding post J3. This permits either negative or positive output to an external earth potential.

Note that with positive output connected to the Earth you should never take measurements with earth referenced instruments such as an oscilloscope. That will create a short circuit and excessive output current could damage the connected instrument’s wiring.

Remote sense is performed with signal relays (K_S1, K_S2), and local sensing is selected when they are not active. Activation of remote sensing is indicated with an LED (LED_S1, LED_S2); two additional wires (or perhaps a 2-wire shielded cable) has to be used to connect sensing inputs to the load. This technique is called Kelvin wiring and is common in high precision electronics work. Caution is required to avoid polarity mismatches. But, even if a polarity mismatch happens, a reverse polarity detection (http://www.envox.hr/eez/bench-power-supply/power-board.html#reverse_polarity) circuit on each Power board will limit output voltage, and an alarm for the MCU will be triggered.

All relays are indirectly driven (Q26-Q29) by a TLC5925 (http://www.ti.com/product/tlc5925) (IC18) which is a 16-channel constant current LED driver. A multiple output LED driver device was chosen because there are 12 LEDs used to indicate various condition during PSU operations:

- Power output is enabled (LED_O1, LED_O2, green, positioned between positive and negative binding posts on each channel)
- Power outputs are coupled in series (or parallel) (LED_SP, red, positioned between Ch1 negative, and Ch2 positive binding posts)
- CC limit mode (LED_CC1, LED_CC2, red, above push-in connector)
- CV limit mode (LED_CV1, LED_CV2, yellow, above CC LED)
- Remote sense is enabled (LED_S1, LED_S2, yellow, above the remote sense input pins of the push-in connector)
- Remote programming is enabled (LED_PROG1, LED_PROG2, red, above the remote sense input pins of the push-in connector) and
- Standby mode (LED_PWR, orange, between reset and the power switch)

All allowable binding posts connections with LED indications and programming codes that can be used for controlling the TLC5925 can be found here (http://www.envox.hr/eez/bench-power-supply/psu-digital-control/psu-binding-posts-section-programming-codes.html). Please note that the TLC5925 is powered with 3.3 V while all connected loads (LEDs and relays) use 5 V. This is not an issue for powering the LEDs because the TLC5925 outputs are constant current (max. current is defined with R130 or ~12.1 mA for 1.8 KΩ).

## Arduino board

The Arduino Shield can work with any 3.3 V Arduino board. Currently, that means only one – the Arduino Due (two :)) which is a 32-bit ARM Cortex-M3 (https://en.wikipedia.org/wiki/ARM_Cortex-M3) based board that comes in “Mega” form-factor. Hopefully more boards with the same form-factor will be available in the future from various Arduino designers (e.g. .org STAR – OTTO (http://http://www.arduino.org/products/boards/arduino-star-otto)) or other sources. Connection with the Arduino board requires 8 connectors (Fig. 8): ICSP, DIGITAL, PWML, PWMH, ADCL, ADCH, COMM and POWER. They are located at the three board sides (with ICSP somewhere in the middle!); we learned that this arrangement is rather impractical when the board must be removed. Close attention is required to avoid bending one or more pins on the Arduino Shield side.

Controlling two channels and all peripherals used 64 I/O pins (http://www.envox.hr/eez/bench-power-supply/psu-digital-control/psu-arduino-shield-pin-mapping.html) (SPI (https://en.wikipedia.org/wiki/Serial_Peripheral_Interface_Bus) lines on ICSP connector were not counted) leaving “only” six pins available for future upgrades. Most of them (26) are assigned to the TFT LCD with its touch-screen display. Using another display with high speed serial interface can potentially reduce that to only 2 or 3 pins (+ SPI). An optional 20-pin FFC connector (X20) for 3.5” Riverdi TFT touch-screen displays is already available on the PCB as a possible migration path to a new more efficient local display solution.

Perhaps it’s worth mentioning that each additional Power board requires only four dedicated I/O pin for control. With existing pin mapping that give room for one additional channel (of course that will also require a new PCB layout). The newly introduced 16-bit I/O expander on the Power board (r5B12) could reduce this to only two I/O pin (+ SPI that is currently shared between all peripherals). The pin mapping of all used pins is described here (http://www.envox.hr/eez/bench-power-supply/psu-digital-control/psu-arduino-shield-pin-mapping.html).

Input power of the Arduino Shield is +5 V, supplied by X16 from the Auxiliary power (http://www.envox.hr/eez/bench-power-supply/psu-auxiliary-supply.html) module. The Arduino Due is a 3.3 V board, but 5 V is used as its power input. It can be powered via the POWER header 5V pin (or from a USB port). An internal 3.3 V LDO regulator is used to adjust the 5 V to 3.3 V for local on board use. That LDO is not used for powering 3.3 V circuits on the Arduino Shield. An additional regulator is used for that purpose (IC22).

## Digital isolators

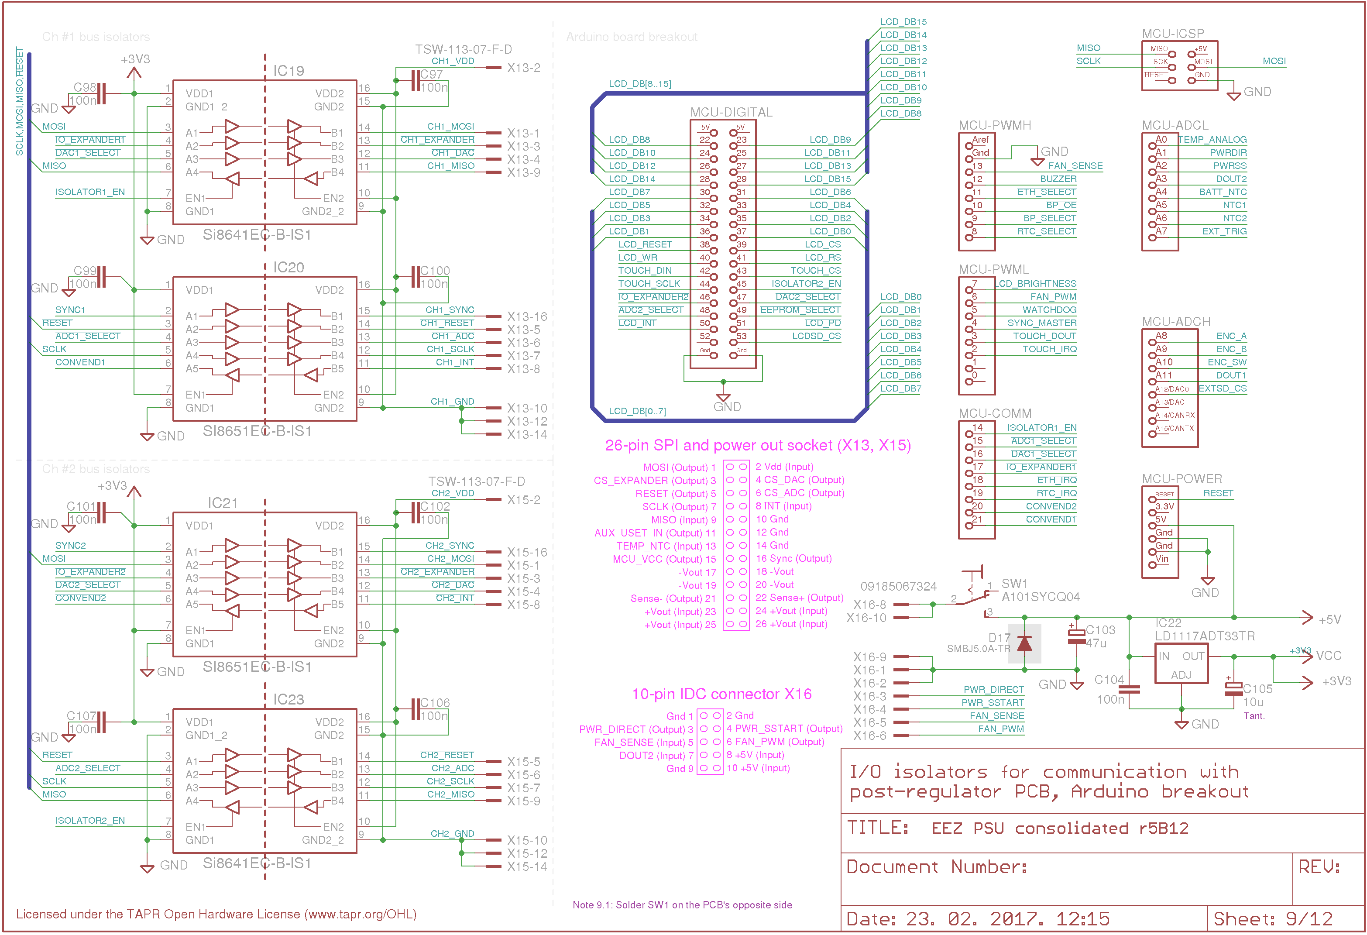
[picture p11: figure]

(http://www.envox.hr/eez/images/arduino_shield_r5b12_sheet9of12.png)Fig. 4: Digital isolators, 3.3V LDO and Arduino board connections

The Arduino Shield can control two PSU channels which are electrically isolated by default; they must remain isolated when they are connected to the Shield. That means digital control signals cannot share the common ground. If such a connection occurs (perhaps via an accidental short), it could be even dangerous when, for instance, channel outputs are connected in serial or when the PSU is used as a dual rail source (positive output from one channel is connected to the another channel's negative output). Digital channel isolation is accomplished using high speed Si86xx series (https://www.silabs.com/products/power/isolators/Pages/Si86xx-Digital-Isolators.aspx) digital isolators.

Two digital isolators are used per channel to isolate 7 outputs and 2 inputs (IC19, IC20 for Ch1 and IC21, IC23 for Ch2). They are SPI lines, chip selects for SPI peripherals on the Power board (ADC, DAC and I/O expander), and Master sync for switching regulators frequency synchronization. The MISO line (Master-in-Slave-out) SPI line requires additional control (ISOLATOR1_EN, ISOLATOR2_EN outputs) to select receiving of data from one channel at a time. Otherwise, data corruption will be inevitable.

## Power board I/O connector

Two 26-pin headers (X13, X15) are used to connect with the Power boards. Functions of the first ten pins follows the ICSP (https://en.wikipedia.org/wiki/In-system_programming) 10-pin header mapping carrying digital signals for SPI, chip selects and supply voltage for the channel side (B side in accordance to Silicon Labs datasheet) of the digital isolators. The rest of the connector is used for various analog signal and power lines as described in table below.

# | I/O name | Active | Description

1 | MOSI | High | MOSI (SPI)
2 | Vdd | Power | Power board +5 V output
3 | CS_EXPANDER | Low | I/O expander chip select
4 | CS_DAC | Low | DAC chip select
5 | RESET | Low | Reset
6 | CS_ADC | Low | ADC chip select
7 | SCLK | High | SCLK (SPI)
8 | INT | Low | I/O expander IRQ (https://en.wikipedia.org/wiki/Interrupt_request_(PC_architecture)) / ADC conversion end
9 | MISO | High | MISO (SPI)
10 | Gnd | Power | Power board ground
11 | AUX_USET_IN | Analog | Remote voltage programming
12 | Gnd | Power | Power board ground
13 | TEMP_NTC | Analog | Power board temperature sensor (NTC)
14 | Gnd | Power | Power board ground
15 | MCU_VCC | Power | Arduino board +3.3 V output
16 | Sync | High | Master sync for switching regulator’s frequency synchronizations
17 | Vout- | Power | Negative power output
18 | Vout- | Power | Negative power output
19 | Vout- | Power | Negative power output
20 | Vout- | Power | Negative power output
21 | Sense- | Analog | Remote voltage sensing negative signal
22 | Sense+ | Analog | Remote voltage sensing positive signal
23 | Vout+ | Power | Positive power output
24 | Vout+ | Power | Positive power output
25 | Vout+ | Power | Positive power output
26 | Vout+ | Power | Positive power output

## I/O peripherals

SPI peripherals might be added to the Arduino Shield (Fig. 8) to provide functions are not regularly available on the Arduino board. In fact, for the Arduino Due that is partially true because its MCU has RTC (Real-time-clock), and even Ethernet. But as far as we know, the former cannot be easily powered from a back-up source when the main power is switched off, and the latter is not exposed to an external connector nor supported through Arduino libraries. The on-board RTC (IC24) supply is backed up with 1 F Supercap (C112) which should be enough for keeping it running for a couple of weeks when the main power is not present.

Ethernet communication is accomplished using (IC26). In addition, an EEPROM (IC25) is added since MCU on Arduino Due does not have any EEPROM memory.

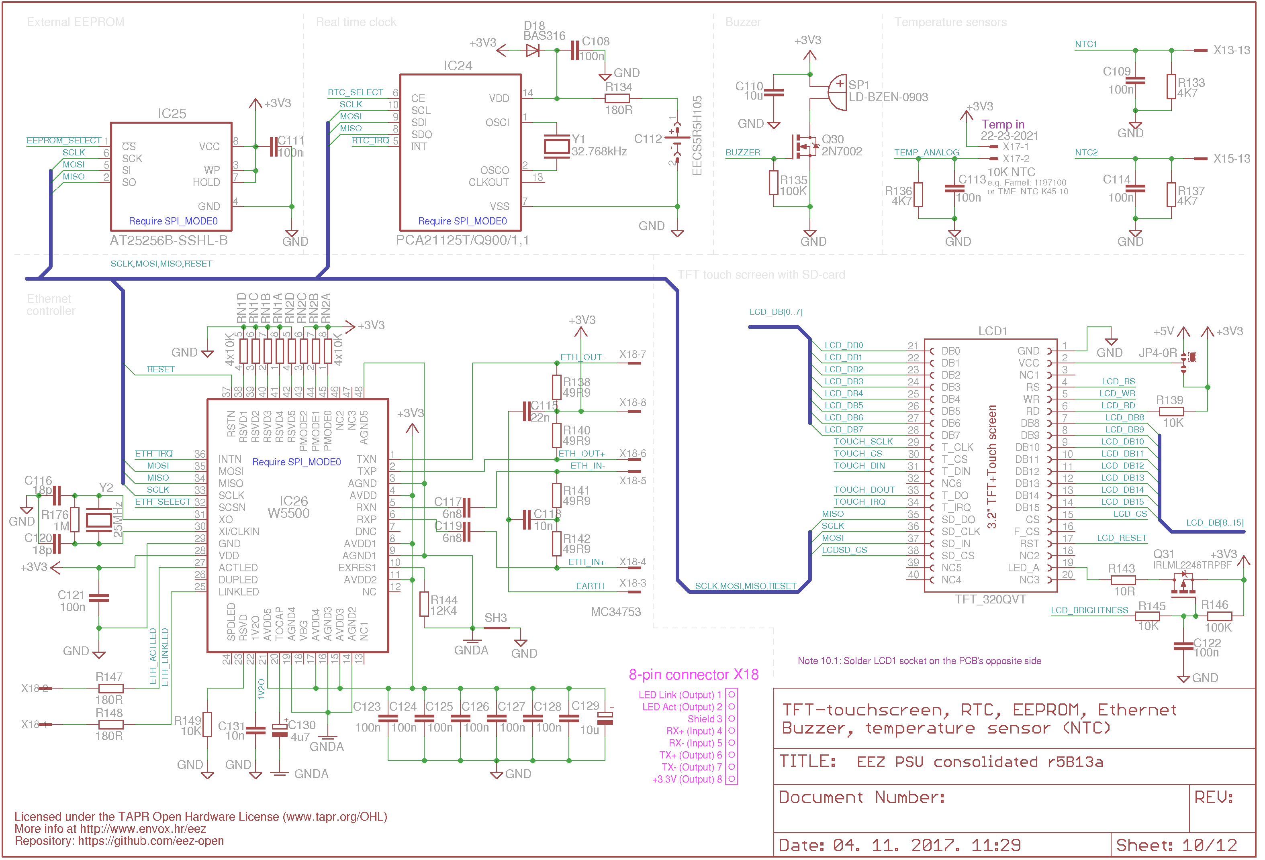
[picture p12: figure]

(http://www.envox.hr/eez/images/arduino_shield_r5b13a_sheet10of12.png)Fig. 5: Arduino Shield peripherals

The TFT display (Fig. 6) has 3.2” diagonal size, 262K (18-bit) colors and 240 x 320 pixels (rotated horizontally!) that gives enough room to display much important information about both channels and system status and messages simultaneously. Color coding could improve the visibility of one or another value amongst the data from various sources. This display unfortunately is not available yet through major suppliers mentioned in the BOM (https://github.com/eez-open/psu-hw/tree/master/Consolidated/BOM), but it can be easily found on any major on-line shopping site (eBay, AliExpress, etc.) by searching for TFT_320QVT. Additionally, the search query could be further narrowed by physical size (3.2 Inch), resolution (240 x 320), and the name of the matching LCD controller (SSD1289 (http://www.solomon-systech.com/en/product/display-ic/smart-tft-lcd-driver-controller/ssd1289/)). The newer display version comes with a new LCD controller (ILI9341); the PSU firmware supports both versions.

This display also comes with SD card slot that can be used as mass storage for such things as data logging, user’s programs, data, etc.

A few words about selection of SPI bus. It’s very common for devices with similar functionality and complexity as the EEZ PSU to use an I²C bus for communication with various peripherals. Devices with such interfaces are in general cheaper, require only two lines for communications (no SCLK and no dedicated chip select for each device is required!), and are well supported with software libraries. I²C can be very beneficial for low end MCUs with low I/O pin count. But that also in general means less processing power and memory which makes them unsuitable for the firmware complexity we need. We have already mentioned that the Arduino board we recommend offers enough I/O ports for addressing 16-bit TFT LCD, various peripherals, and at least two Power board (up to 3, or 4 if SPI is used for touch-screen controller). Anyway, SPI bus offers more flexible device addressing and much faster communication which makes the PSU more responsive.

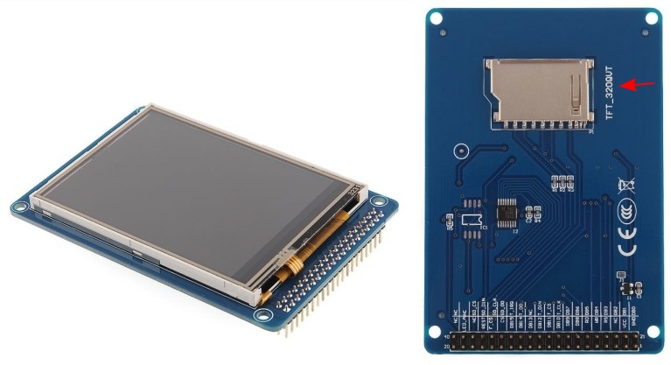
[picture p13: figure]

(http://www.envox.hr/eez/images/ebay_320qvt_mark.jpg)Fig. 6: 3.2" Color TFT display with touch screen and SD-card socket

Not all peripherals requires SPI nor any other mean of digital bus interfacing. Such examples are:

- buzzer (SP1) that is driven with PWM output (via Q30),
- analog inputs for temperature sensors (TEMP_ANALOG, NTC1, NTC2 inputs),
- isolated analog input for temperature sensor (BATT_NTC, see Fig. Error: Reference source not found),
- TFT display backlight adjustment driven with PWM output (via Q31),
- incremental encoder (ENC_A, ENC_B, see Fig. Error: Reference source not found)
- external digital trigger input (EXT_TRIG, see Fig. Error: Reference source not found) and
- power relay output (DOUT2)

## SPI modes

Working with SPI peripherals requires selection of the mode of operation. Four modes are available and defined by serial clock (SCK or SCLK) polarity and phase. For example the Arduino IDE (https://www.arduino.cc/en/Reference/SPISettings) provides four data constants for them: SPI_MODE0, SPI_MODE1, SPI_MODE2 and SPI_MODE3. Selecting a right mode of operation can be frustrating when IC manufacturers specifications or hardware implementation are unclear. We learned that if an IC is not damaged or improperly connected but IC response is erratic, checking the SPI mode in use is the first thing that should be done! If you are not sure what mode to use, the fastest way to establish meaningful communication is to simply select them one by one and monitor the results (i.e. the outputs are set correctly, or the returned data register content is equal to the one that has been set, etc.).

## Remote communication

The EEZ PSU can communicate with the external world using USB or Ethernet. The on-board Ethernet controller (IC26) is only missing a RJ-45 modular jack for a LAN cable connection. The connector is to be placed on the Auxiliary power (http://www.envox.hr/eez/bench-power-supply/psu-auxiliary-supply.html) module which is in turn mounted directly on the inner side of the enclosure’s rear panel. The USB-B connector is similar – it’s located near the Ethernet RJ-45. It is not connected to the Arduino Shield, but rather directly to the Arduino Due's USB programming port. A 5-pin to micro-USB cable (as shown in Fig. 7) is used.

## Supply-voltage supervision, watchdog and reset

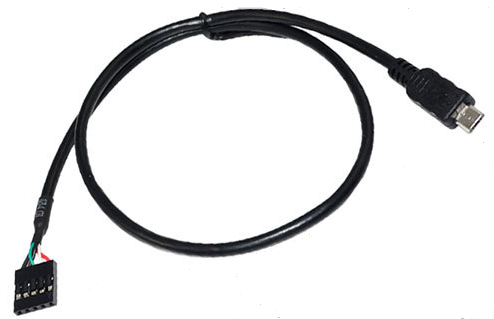
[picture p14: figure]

(http://www.envox.hr/eez/images/micro-usb-to-5pin.png)Fig. 7: Micro USB to 5-pin cable

A TPS3705-33 (http://www.ti.com/product/TPS3705-33) (IC31) is used to improve overall reliability of the PSUs digital controls, and provides the following functions:

- Supervises the 3.3 V supply provided by IC22 (Fig. 8), and generates a 200 ms RESET pulse on power up and power fail,
- Provides a “clean” (i.e. well defined) reset when manual reset tactile switch (SW3, Fig. Error: Reference source not found) is used and
- Generates reset if the MCU, due to hardware or firmware issues, misses sending a WATCHDOG signal within 1 second.

The reset signal generated by IC31 is also used to immediately deactivate main power by pulling down the control outputs (PWR_DIRECT, PWR_SSTART) of both triacs on the Auxiliary power board via IC29 as additional precautionary measure against unexpected conditions. The same scheme is used with the power relay DOUT2 control.

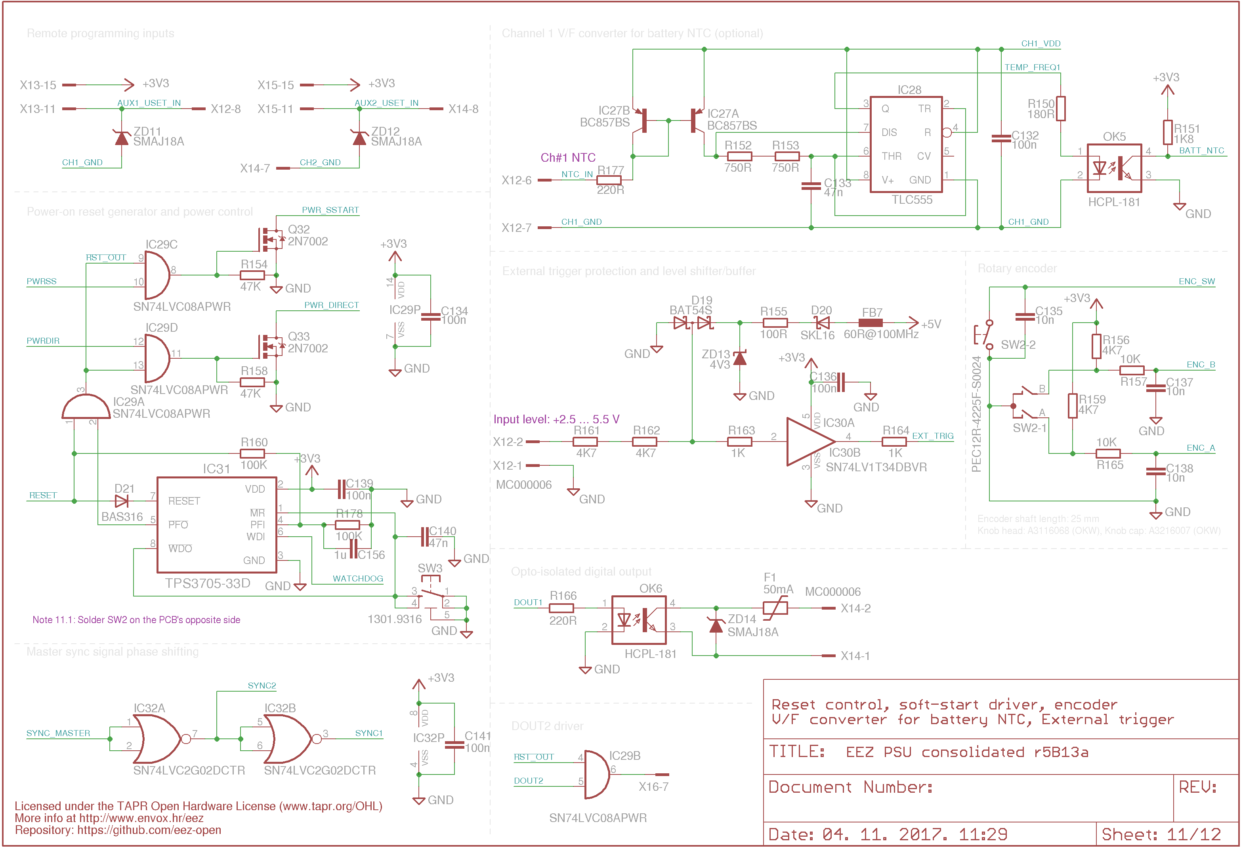
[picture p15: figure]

(http://www.envox.hr/eez/images/arduino_shield_r5b13a_sheet11of12.png)Fig. 8: Reset supervision, master sync phase shifter and various non-SPI periperals

## Special I/O

The Arduino Shield has two special inputs that can be used for external control of the PSU. Both inputs are wired to the X12 8-pin push-in connector above the Ch1 binding posts. The first is an analog input which can be used with a 10 kΩ temperature sensor which is the standard value for batteries which has a temperature monitoring output. In addition to monitoring battery during fast charging, it can be used to controlling PSU’s channels for different sources. The BAT_NTC output is a digital output (the popular 555 timer, IC28, acts as a Voltage-to-Frequency converter) because it’s easier to isolate it while maintaining good accuracy then an analog signal. For better linearity, the input resistor is not connected directly to the timer, but to a current mirror (https://en.wikipedia.org/wiki/Current_mirror) circuit is used (IC27). R177 is used to limit current in case the NTC input are incidentally shorted to ground (if such a fault condition lasts for a prolonged period, that could cause loss of PWRGOOD signal on Ch1 upon which firmware will push the entire PSU into standby mode). OK5 is used as an optical isolator.

Another input is purly digital and can be used for triggering various PSU’s functions via an external digital signal which can be connected, for example, to a D.U.T. An MCU input is used for connecting external signal but the connection is not direct – direct connection to some external signal can easily induce erratic behavior or even irreversible damage in the MCU! Therefore, the MCU input is protected against over-voltage and reverse polarity conditions with D19 and pre-polarized ZD13. R161-R163 limit current to the protection circuit, and IC30 behaves as a buffer and level-shifter. Finally, R164 limits the current that can be drawn by the MCU input. Thanks to the level-shifting feature, an input signal can be anything between approx. 2.5 and 5 V and still work properly.

The DOUT line is an opto-coupled (OK6) and protected (F1, ZD14) MCU output that can be used for triggering external devices.

## Switching regulators frequency synchronization

The PSU has two switching pre-regulators which, without synchronization, will work with different switching frequencies. That could increase EMI (https://en.wikipedia.org/wiki/Electromagnetic_interference) (i.e. radiated noise from the PSU) and can result in higher ripple and noise on its outputs. As a result, frequency synchronization can be supported in firmware. When selected, the “master clock” is generated by Arduino Due (SYNC_MASTER, Fig. 8) and distributed to switching pre-regulators on the Power board (http://www.envox.hr/eez/bench-power-supply/power-board.html)s (http://www.envox.hr/eez/bench-power-supply/power-board.html). The master signal (SYNC_IN) then arrives at a Power board via IC32: as SYNC1 for Ch1 and intentionally inverted SYNC2 for Ch2. Switching noise on a channel outputs will be 180o out of phase which should decrease total noise energy radiated, especially when both channels are coupled in parallel.

## PCB layout

A two layer PCB (220 x 74 mm) holds not only the Arduino board but also the TFT LCD, all the binding posts, the LEDs, switches and plug-in connectors. The board was laid out in Eagle, but the autorouter (http://www.cadsoftusa.com/eagle-pcb-design-software/autorouter/) was not used. In that way, only three cables are required to connect with the rest of the system. Power board connectors (X13, X15), power input (X16), and Ethernet (X18) are soldered on the top side of the board. Binding posts (including protective earth), LEDs, switches and push-in connectors are soldered on the bottom side.

The distance between the PCB and the enclosure’s front panel is 18 mm, therefore the binding posts we've selected cannot be connected directly to the connection points on the PCB. A screwed spacer sleeve mentioned in the BOM has to be used. See the building instructions (http://www.envox.hr/eez/bench-power-supply/building-instructions.html#instr_wire).

Some parts are located in the area beneath the Arduino board (e.g., RTC, or EEPROM), therefore they have to be soldered before the Arduino is plugged in.

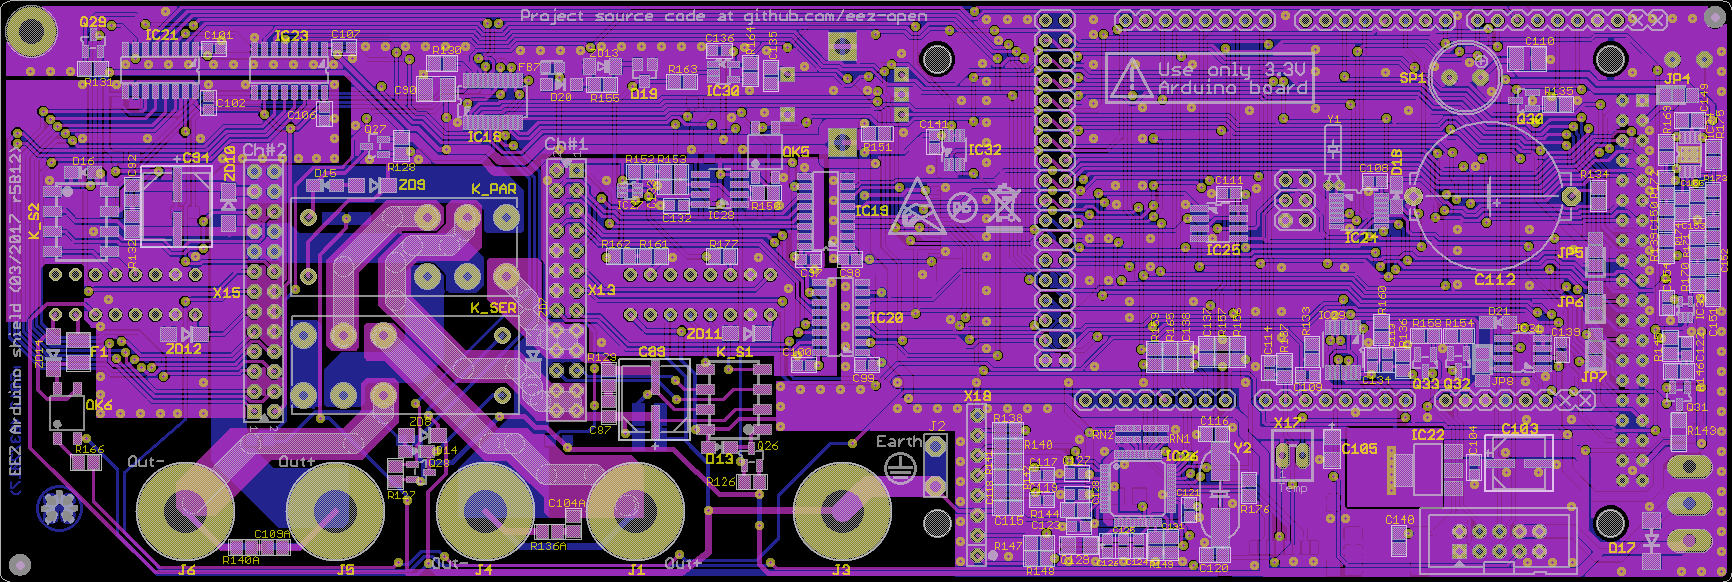
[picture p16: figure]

(http://www.envox.hr/eez/images/pcb_arduino_shield_r5b12_all.png)Fig. 9: PCB layout r5B12 (both sides)

For possible modifications and tweaking visit the Hacking area (http://www.envox.hr/eez/bench-power-supply/hacking-area.html).

Revision: 0.2 1 (of 12) Last modified: 2017-05-08

DRAFT – PSU arduino shield r5B13a

Last modified: 2017-05-08 12 (of 12) Doc. version: 0.2

Revision: 0.2 11 (of 12) Last modified: 2017-05-08

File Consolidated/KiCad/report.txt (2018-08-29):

Info: Processing component “ZD8:/5B870BAA/920AA273:EEZ PSU consolidated r5B13a:DO214AC”.

Info: Processing component “C23:/5B86F281/69B575A3:EEZ PSU consolidated r5B13a:EC1206”.

Info: Processing component “C21:/5B86F281/C8F27F71:EEZ PSU consolidated r5B13a:EC1206”.

Info: Processing component “C130:/5B871692/E7304FE7:EEZ PSU consolidated r5B13a:EC1206”.

Info: Processing component “C57:/5B86FCC4/22FDA0A9:EEZ PSU consolidated r5B13a:EC1206”.

Info: Processing component “IC15:/5B870870/B577E39F:EEZ PSU consolidated r5B13a:DRL5”.

Info: Processing component “ZD14:/5B871CD8/723E3B3D:EEZ PSU consolidated r5B13a:DO214AC”.

Info: Processing component “ZD11:/5B871CD8/7B818DAF:EEZ PSU consolidated r5B13a:DO214AC”.

Info: Processing component “ZD10:/5B870BAA/5F3B6E90:EEZ PSU consolidated r5B13a:DO214AC”.

Info: Processing component “ZD9:/5B870BAA/DA83024E:EEZ PSU consolidated r5B13a:DO214AC”.

Info: Processing component “C105:/5B8711C3/25B9E12B:EEZ PSU consolidated r5B13a:EC1206”.

Info: Processing component “ZD7:/5B870BAA/9FA9C7F8:EEZ PSU consolidated r5B13a:DO214AC”.

Info: Processing component “ZD6:/5B870870/4F60ED90:EEZ PSU consolidated r5B13a:DO214AC”.

Info: Changing symbol “ZD6:/5B870870/4F60ED90” pin “C” net name from “Net-(K_DOUT-PadA2)” to “Net-(K_DOUT1-PadA2)”.

Info: Processing component “ZD12:/5B871CD8/3AE115BD:EEZ PSU consolidated r5B13a:DO214AC”.

Info: Processing component “D17:/5B8711C3/10BF0990:EEZ PSU consolidated r5B13a:DO214AA”.

Info: Processing component “ZD15:/5B8722D3/D3FB81E3:EEZ PSU consolidated r5B13a:DO214AA”.

Info: Processing component “ZD1:/5B86EEA2/376526C0:EEZ PSU consolidated r5B13a:DO214AA”.

Info: Processing component “ZD5:/5B870419/5EA163C9:EEZ PSU consolidated r5B13a:DO201-BIDIR”.

Info: Processing component “ZD4:/5B870419/4BC96379:EEZ PSU consolidated r5B13a:DO201-BIDIR”.

Info: Processing component “FM6:/5B870BAA/17039B8E:EEZ PSU consolidated r5B13a:FIDUCIAL_DUAL”.

Info: Processing component “OK3:/5B870419/E70EF526:EEZ PSU consolidated r5B13a:HCPL-181”.

Info: Processing component “OK6:/5B871CD8/248DC63E:EEZ PSU consolidated r5B13a:HCPL-181”.

Info: Processing component “OK5:/5B871CD8/6FC3A3A4:EEZ PSU consolidated r5B13a:HCPL-181”.

Info: Processing component “Y2:/5B871692/5E2E8076:EEZ PSU consolidated r5B13a:HC-49_4H”.

Info: Processing component “K_S2:/5B870BAA/E1A557B3:EEZ PSU consolidated r5B13a:G6K-2F”.

Info: Processing component “K_S1:/5B870BAA/E2180004:EEZ PSU consolidated r5B13a:G6K-2F”.

Info: Processing component “X20:/5B8722D3/DFA9EBB3:EEZ PSU consolidated r5B13a:FPC-20_ROTATED”.

Info: Processing component “FM4:/5B870419/F73411F7:EEZ PSU consolidated r5B13a:FIDUCIAL_DUAL”.

Info: Processing component “FM5:/5B870BAA/2C358A67:EEZ PSU consolidated r5B13a:FIDUCIAL_DUAL”.

Info: Processing component “OK2:/5B870419/94B9D4CB:EEZ PSU consolidated r5B13a:DIL6-SMD”.

Info: Processing component “FM3:/5B870419/A2DB92E8:EEZ PSU consolidated r5B13a:FIDUCIAL_DUAL”.

Info: Processing component “FM2:/5B86EEA2/8BCA1F73:EEZ PSU consolidated r5B13a:FIDUCIAL_DUAL”.

Info: Processing component “FM1:/5B86EEA2/DCDC82BF:EEZ PSU consolidated r5B13a:FIDUCIAL_DUAL”.

Info: Processing component “F1:/5B871CD8/268E53C9:EEZ PSU consolidated r5B13a:F1210”.

Info: Processing component “C145:/5B8722D3/8E9C6108:EEZ PSU consolidated r5B13a:ECAP7.5_18”.

Info: Processing component “C146:/5B8722D3/AEEEC613:EEZ PSU consolidated r5B13a:ECAP7.5_18”.

Info: Processing component “SW2:/5B871CD8/9E8CEC31:EEZ PSU consolidated r5B13a:EC12E_SW”.

Info: Processing component “C129:/5B871692/49DD5F01:EEZ PSU consolidated r5B13a:EC1206”.

Info: Processing component “C31:/5B86F281/FDB3934F:EEZ PSU consolidated r5B13a:EC1206”.

Info: Processing component “C110:/5B871692/9C377AE7:EEZ PSU consolidated r5B13a:C1210”.

Info: Processing component “C16:/5B86EEA2/020271E7:EEZ PSU consolidated r5B13a:C1210”.

Info: Processing component “C22:/5B86F281/5A436AB8:EEZ PSU consolidated r5B13a:C1210”.

Info: Processing component “C24:/5B86F281/8D4DE143:EEZ PSU consolidated r5B13a:C1210”.

Info: Processing component “C29:/5B86F281/46B0858E:EEZ PSU consolidated r5B13a:C1210”.

Info: Processing component “C30:/5B86F281/EA6B2BE4:EEZ PSU consolidated r5B13a:C1210”.

Info: Processing component “C55:/5B86FCC4/7B3A80DA:EEZ PSU consolidated r5B13a:C1210”.

Info: Processing component “C95:/5B870BAA/BABD5995:EEZ PSU consolidated r5B13a:C1210”.

Info: Processing component “C91:/5B870BAA/20CAF282:EEZ PSU consolidated r5B13a:C1210”.

Info: Processing component “C90:/5B870BAA/773E810E:EEZ PSU consolidated r5B13a:C1210”.

Info: Processing component “C10:/5B86EEA2/3100FCDB:EEZ PSU consolidated r5B13a:C1210”.

Info: Processing component “C88:/5B870BAA/7EF724FA:EEZ PSU consolidated r5B13a:C1210”.

Info: Processing component “C143:/5B8722D3/361B3E2E:EEZ PSU consolidated r5B13a:C1206”.

Info: Processing component “C144:/5B8722D3/9508029C:EEZ PSU consolidated r5B13a:C1206”.

Info: Processing component “C147:/5B8722D3/925137CC:EEZ PSU consolidated r5B13a:C1206”.

Info: Processing component “C148:/5B8722D3/E420C4A9:EEZ PSU consolidated r5B13a:C1206”.

Info: Processing component “C142:/5B8722D3/6DBBFFF5:EEZ PSU consolidated r5B13a:C1206”.

Info: Processing component “C1:/5B86EEA2/12BF0275:EEZ PSU consolidated r5B13a:C1206”.

Info: Processing component “C4:/5B86EEA2/BD10B666:EEZ PSU consolidated r5B13a:C1206”.

Info: Processing component “C8:/5B86EEA2/EA77A757:EEZ PSU consolidated r5B13a:C1206”.

Info: Processing component “C94:/5B870BAA/967BC465:EEZ PSU consolidated r5B13a:CAPAE830X650N”.

Info: Processing component “OK1:/5B870419/02324650:EEZ PSU consolidated r5B13a:DIL6-SMD”.

Info: Processing component “IC10:/5B86FCC4/C438D0CC:EEZ PSU consolidated r5B13a:DGK8-M”.

Info: Processing component “L5:/5B870419/50948D1E:EEZ PSU consolidated r5B13a:DE0704”.

Info: Processing component “C27:/5B86F281/14B3F210:EEZ PSU consolidated r5B13a:C_6032-28R”.

Info: Processing component “RN1:/5B871692/374665EF:EEZ PSU consolidated r5B13a:CAY16”.

Info: Processing component “RN2:/5B871692/0EAF5119:EEZ PSU consolidated r5B13a:CAY16”.

Info: Processing component “C96:/5B870BAA/5E5D6F36:EEZ PSU consolidated r5B13a:CAPAE830X650N”.

Info: Processing component “C3:/5B86EEA2/A7483AD5:EEZ PSU consolidated r5B13a:CAPAE830X650N”.

Info: Processing component “C86:/5B870BAA/21DCFD96:EEZ PSU consolidated r5B13a:CAPAE830X650N”.

Info: Processing component “OK4:/5B870419/502154E6:EEZ PSU consolidated r5B13a:HCPL-181”.

Info: Processing component “C89:/5B870BAA/0CD94EC6:EEZ PSU consolidated r5B13a:CAPAE830X650N”.

Info: Processing component “C13:/5B86EEA2/1C4FC955:EEZ PSU consolidated r5B13a:CAPAE830X1050N”.

Info: Processing component “C78:/5B870419/E4113A87:EEZ PSU consolidated r5B13a:CAPAE660X610N”.

Info: Processing component “C80:/5B870419/EB6B3C9D:EEZ PSU consolidated r5B13a:CAPAE660X610N”.

Info: Processing component “C77:/5B870419/7277BEE9:EEZ PSU consolidated r5B13a:CAPAE660X610N”.

Info: Processing component “C103:/5B8711C3/545840A3:EEZ PSU consolidated r5B13a:CAPAE660X610N”.

Info: Processing component “C93:/5B870BAA/E9C3B98D:EEZ PSU consolidated r5B13a:C1210”.

Info: Processing component “C5:/5B86EEA2/000A48F2:EEZ PSU consolidated r5B13a:C1210”.

Info: Processing component “C6:/5B86EEA2/AFAB1000:EEZ PSU consolidated r5B13a:C1210”.

Info: Processing component “R41:/5B86F516/25335C33:EEZ PSU consolidated r5B13a:R0805”.

Info: Processing component “R27:/5B86F516/D54F13E9:EEZ PSU consolidated r5B13a:R0805”.

Info: Processing component “R28:/5B86F516/DCA88CDA:EEZ PSU consolidated r5B13a:R0805”.

Info: Processing component “R29:/5B86F516/5A394440:EEZ PSU consolidated r5B13a:R0805”.

Info: Processing component “R30:/5B86F516/37144564:EEZ PSU consolidated r5B13a:R0805”.

Info: Processing component “JP10:/5B870870/04432732:EEZ PSU consolidated r5B13a:ZL303-03P”.

Info: Processing component “R32:/5B86F516/B43988F7:EEZ PSU consolidated r5B13a:R0805”.

Info: Processing component “R34:/5B86F516/580752BB:EEZ PSU consolidated r5B13a:R0805”.

Info: Processing component “R136A1:/5B870BAA/2D5E3D32:EEZ PSU consolidated r5B13a:R0805”.

Info: Adding new symbol “R136A1:/5B870BAA/2D5E3D32” footprint “EEZ PSU consolidated r5B13a:R0805”.

Info: Processing component “R24:/5B86F281/F9A5DEFA:EEZ PSU consolidated r5B13a:R0805”.

Info: Processing component “R177:/5B871CD8/5AB57C08:EEZ PSU consolidated r5B13a:R0805”.

Info: Processing component “R178:/5B871CD8/3A504CB3:EEZ PSU consolidated r5B13a:R0805”.

Info: Processing component “R160:/5B871CD8/75988E61:EEZ PSU consolidated r5B13a:R0805”.

Info: Processing component “R36:/5B86F516/D53C8267:EEZ PSU consolidated r5B13a:R0805”.

Info: Processing component “R38:/5B86F516/4E46F10B:EEZ PSU consolidated r5B13a:R0805”.

Info: Processing component “R42:/5B86F516/F667BDE4:EEZ PSU consolidated r5B13a:R0805”.

Info: Processing component “R40:/5B86F516/F99EA41E:EEZ PSU consolidated r5B13a:R0805”.

Info: Processing component “R37:/5B86F516/9F84A1F3:EEZ PSU consolidated r5B13a:R0805”.

Info: Processing component “R39:/5B86F516/8E96C20E:EEZ PSU consolidated r5B13a:R0805”.

Info: Processing component “R101:/5B870139/CC688F37:EEZ PSU consolidated r5B13a:R0805”.

Info: Adding new symbol “R78B1:/5B86FCC4/E8D586BE” footprint “EEZ PSU consolidated r5B13a:R0805”.

Info: Processing component “R2:/5B86EEA2/910CEFCB:EEZ PSU consolidated r5B13a:R0805”.

Info: Processing component “R3:/5B86EEA2/2A684572:EEZ PSU consolidated r5B13a:R0805”.

Info: Processing component “R5:/5B86EEA2/4AFF4A0D:EEZ PSU consolidated r5B13a:R0805”.

Info: Processing component “R6:/5B86EEA2/C3B56805:EEZ PSU consolidated r5B13a:R0805”.

Info: Processing component “R7:/5B86EEA2/CE756263:EEZ PSU consolidated r5B13a:R0805”.

Info: Processing component “R8:/5B86EEA2/1338A13A:EEZ PSU consolidated r5B13a:R0805”.

Info: Processing component “R10:/5B86EEA2/41718522:EEZ PSU consolidated r5B13a:R0805”.

Info: Processing component “R25:/5B86F281/337EF62C:EEZ PSU consolidated r5B13a:R0805”.

Info: Processing component “IC13:/5B86FCC4/770BEB2D:EEZ PSU consolidated r5B13a:PW(R-PDSO-G16)”.

Info: Processing component “R100:/5B870139/D029C05C:EEZ PSU consolidated r5B13a:R0805”.

Info: Processing component “R99:/5B870139/6C1B4D68:EEZ PSU consolidated r5B13a:R0805”.

Info: Processing component “R98:/5B870139/937924BB:EEZ PSU consolidated r5B13a:R0805”.

Info: Processing component “R97:/5B870139/F5A6D381:EEZ PSU consolidated r5B13a:R0805”.

Info: Processing component “R96:/5B870139/E227B9CE:EEZ PSU consolidated r5B13a:R0805”.

Info: Processing component “R95:/5B870139/DBF7C3AD:EEZ PSU consolidated r5B13a:R0805”.

Info: Processing component “R94:/5B870139/39937A76:EEZ PSU consolidated r5B13a:R0805”.

Info: Processing component “R93:/5B870139/18C871D4:EEZ PSU consolidated r5B13a:R0805”.

Info: Processing component “R180:/5B86F516/83161B66:EEZ PSU consolidated r5B13a:R0805”.

Info: Processing component “JP4:/5B871692/193933AB:EEZ PSU consolidated r5B13a:JP3-CUT”.

Info: Processing component “LED_S2:/5B870BAA/B0F5C562:EEZ PSU consolidated r5B13a:LED_0805”.

Info: Processing component “LED_PWR1:/5B870BAA/D94A45ED:EEZ PSU consolidated r5B13a:LED_0805”.

Info: Adding new symbol “LED_PWR1:/5B870BAA/D94A45ED” footprint “EEZ PSU consolidated r5B13a:LED_0805”.

Info: Processing component “LED_O2:/5B870BAA/A9012F9B:EEZ PSU consolidated r5B13a:LED_0805”.

Info: Processing component “LED_S1:/5B870BAA/C17797F5:EEZ PSU consolidated r5B13a:LED_0805”.

Info: Processing component “SP1:/5B871692/F99D3381:EEZ PSU consolidated r5B13a:LD-BZEN-0903”.

Info: Processing component “SP2:/5B8722D3/2E4EEBD6:EEZ PSU consolidated r5B13a:LD-BZEN-0903”.

Info: Processing component “LCD1:/5B871692/FD8AA809:EEZ PSU consolidated r5B13a:LCD_TFT_9341_MIRROR”.

Info: Processing component “X11:/5B870870/5F2C949E:EEZ PSU consolidated r5B13a:KUSBVX-BS1N”.

Info: Processing component “LED_CV1:/5B870BAA/C4F1DEAE:EEZ PSU consolidated r5B13a:LED_0805”.

Info: Processing component “JP3:/5B86FCC4/8182258E:EEZ PSU consolidated r5B13a:JP3-CUT”.

Info: Processing component “JP2:/5B86F516/BAFA783C:EEZ PSU consolidated r5B13a:JP3-CUT”.

Info: Processing component “JP1:/5B86EEA2/0B60073D:EEZ PSU consolidated r5B13a:JP3-CUT”.

Info: Processing component “L4:/5B86EEA2/F9CAFA06:EEZ PSU consolidated r5B13a:IHLP-2020BZ-11”.

Info: Processing component “L3:/5B86EEA2/0B156C27:EEZ PSU consolidated r5B13a:IHLP-2020BZ-11”.

Info: Processing component “X5:/5B870419/F6666F73:EEZ PSU consolidated r5B13a:IDC-10PIN”.

Info: Processing component “X16:/5B8711C3/BB9D6A3E:EEZ PSU consolidated r5B13a:IDC-10PIN”.

Info: Processing component “X8:/5B870870/ABF727A1:EEZ PSU consolidated r5B13a:HEADER_8-PIN”.

Info: Processing component “X18:/5B871692/B97B101F:EEZ PSU consolidated r5B13a:HEADER_8-PIN”.

Info: Processing component “IC1:/5B86EEA2/28002D22:EEZ PSU consolidated r5B13a:LTC_05-08-1666”.

Info: Processing component “J2:/5B870BAA/D83AA60C:EEZ PSU consolidated r5B13a:PCB_TAB-4.8MM”.

Info: Processing component “TR1:/5B870419/F6D25935:EEZ PSU consolidated r5B13a:PCB_ACDC_VTX_5W_DUAL”.

Info: Processing component “C15:/5B86EEA2/707DE72D:EEZ PSU consolidated r5B13a:PANASONIC_F”.

Info: Processing component “ZD13:/5B871CD8/3DFB0441:EEZ PSU consolidated r5B13a:MINIMELF”.

Info: Processing component “X3:/5B870419/3628F368:EEZ PSU consolidated r5B13a:MINIFIT_6659-5”.

Info: Processing component “X1:/5B86EEA2/9DC1DC97:EEZ PSU consolidated r5B13a:MINIFIT_39301039”.

Info: Processing component “X12:/5B870BAA/756A31A6:EEZ PSU consolidated r5B13a:MC000006_MIRROR”.

Info: Processing component “X14:/5B870BAA/E29D80B6:EEZ PSU consolidated r5B13a:MC000006_MIRROR”.

Info: Processing component “SW1:/5B8711C3/5427593F:EEZ PSU consolidated r5B13a:M9040P”.

Info: Processing component “C33:/5B86F516/23146F2A:EEZ PSU consolidated r5B13a:C1206”.

Info: Processing component “LED_PROG2:/5B870BAA/FC8E073F:EEZ PSU consolidated r5B13a:LED_HSMH-C170”.

Info: Processing component “LED_PROG1:/5B870BAA/DC206D80:EEZ PSU consolidated r5B13a:LED_HSMH-C170”.

Info: Processing component “LED_CC2:/5B870BAA/5F9387C2:EEZ PSU consolidated r5B13a:LED_HSMH-C170”.

Info: Processing component “LED_CC1:/5B870BAA/AA4A179D:EEZ PSU consolidated r5B13a:LED_HSMH-C170”.

Info: Processing component “LED_SP1:/5B870BAA/3BFBD0DA:EEZ PSU consolidated r5B13a:LED_HSMH-C170”.

Info: Adding new symbol “LED_SP1:/5B870BAA/3BFBD0DA” footprint “EEZ PSU consolidated r5B13a:LED_HSMH-C170”.

Info: Processing component “LED_O1:/5B870BAA/E6235207:EEZ PSU consolidated r5B13a:LED_0805”.

Info: Processing component “LED_CV2:/5B870BAA/CD1F1A1A:EEZ PSU consolidated r5B13a:LED_0805”.

Info: Processing component “C104:/5B8711C3/148A259C:EEZ PSU consolidated r5B13a:C0603”.

Info: Processing component “C124:/5B871692/1B02BFFC:EEZ PSU consolidated r5B13a:C0603”.

Info: Processing component “C123:/5B871692/0E4D5A9F:EEZ PSU consolidated r5B13a:C0603”.

Info: Processing component “C121:/5B871692/6DA49C0D:EEZ PSU consolidated r5B13a:C0603”.

Info: Processing component “C97:/5B8711C3/7346883D:EEZ PSU consolidated r5B13a:C0603”.

Info: Processing component “C98:/5B8711C3/943EC404:EEZ PSU consolidated r5B13a:C0603”.

Info: Processing component “C99:/5B8711C3/FC3E0017:EEZ PSU consolidated r5B13a:C0603”.

Info: Processing component “C100:/5B8711C3/78FB91F5:EEZ PSU consolidated r5B13a:C0603”.

Info: Processing component “C101:/5B8711C3/907DB711:EEZ PSU consolidated r5B13a:C0603”.

Info: Processing component “C119:/5B871692/BB7E6586:EEZ PSU consolidated r5B13a:C0603”.

Info: Processing component “C125:/5B871692/B74BB10E:EEZ PSU consolidated r5B13a:C0603”.

Info: Processing component “C106:/5B8711C3/B59270D5:EEZ PSU consolidated r5B13a:C0603”.

Info: Processing component “C107:/5B8711C3/E278C145:EEZ PSU consolidated r5B13a:C0603”.

Info: Processing component “C108:/5B871692/9CDF8123:EEZ PSU consolidated r5B13a:C0603”.

Info: Processing component “C117:/5B871692/5771DF73:EEZ PSU consolidated r5B13a:C0603”.

Info: Processing component “C122:/5B871692/476AB021:EEZ PSU consolidated r5B13a:C0603”.

Info: Processing component “J4:/5B870BAA/FBE157E1:EEZ PSU consolidated r5B13a:BP_5_12”.

Info: Processing component “J6:/5B870BAA/C7D440D3:EEZ PSU consolidated r5B13a:BP_5_12”.

Info: Processing component “J1:/5B870BAA/458172F0:EEZ PSU consolidated r5B13a:BP_5_12”.

Info: Processing component “J3:/5B870BAA/00083527:EEZ PSU consolidated r5B13a:BP_5_12”.

Info: Processing component “C109:/5B871692/382146EA:EEZ PSU consolidated r5B13a:C0603”.

Info: Processing component “C72:/5B870139/D56A278D:EEZ PSU consolidated r5B13a:C0603”.

Info: Processing component “C132:/5B871CD8/AF4866D0:EEZ PSU consolidated r5B13a:C0603”.

Info: Processing component “C81:/5B870870/FEF5F493:EEZ PSU consolidated r5B13a:C0603”.

Info: Processing component “C82:/5B870870/F8A07DF4:EEZ PSU consolidated r5B13a:C0603”.

Info: Processing component “C83:/5B870870/C0A7ABDA:EEZ PSU consolidated r5B13a:C0603”.

Info: Processing component “C84:/5B870870/249F87AB:EEZ PSU consolidated r5B13a:C0603”.

Info: Processing component “C85:/5B870870/00EB8535:EEZ PSU consolidated r5B13a:C0603”.

Info: Processing component “C128:/5B871692/D8CB4E4A:EEZ PSU consolidated r5B13a:C0603”.

Info: Processing component “C127:/5B871692/8D62675D:EEZ PSU consolidated r5B13a:C0603”.

Info: Processing component “J5:/5B870BAA/7D54D00B:EEZ PSU consolidated r5B13a:BP_5_12”.

Info: Processing component “C9:/5B86EEA2/93F3FA2A:EEZ PSU consolidated r5B13a:C0603”.

Info: Processing component “C49:/5B86F516/F533AE70:EEZ PSU consolidated r5B13a:C0603”.

Info: Processing component “C139:/5B871CD8/7021623C:EEZ PSU consolidated r5B13a:C0603”.

Info: Processing component “C141:/5B871CD8/264A421D:EEZ PSU consolidated r5B13a:C0603”.

Info: Processing component “C154:/5B8722D3/8DD2A69A:EEZ PSU consolidated r5B13a:C0603”.

Info: Processing component “C136:/5B871CD8/5F2803E5:EEZ PSU consolidated r5B13a:C0603”.

Info: Processing component “C20:/5B86F281/12BF572B:EEZ PSU consolidated r5B13a:C0603”.

Info: Processing component “C32:/5B86F516/3554C70B:EEZ PSU consolidated r5B13a:C0603”.

Info: Processing component “C102:/5B8711C3/5504E658:EEZ PSU consolidated r5B13a:C0603”.

Info: Removing unused footprint “LED_PWR:/5B870BAA/D94A45ED”.

Info: Removing unused footprint “U$5:”.

Info: Removing unused footprint “U$6:”.

Info: Removing unused footprint “U$7:”.

Info: Removing unused footprint “U$8:”.

Info: Removing unused footprint “U$9:”.

Info: Removing unused footprint “EEZ_SIGNATURE2:”.

Info: Removing unused footprint “MCU:/5B8711C3/38E59275”.

Info: Removing unused footprint “K_SER:/5B870BAA/9978EF33”.

Info: Removing unused footprint “K_PAR:/5B870BAA/DEAF6977”.

Info: Removing unused footprint “U$1:”.

Info: Removing unused footprint “LED_SP:/5B870BAA/3BFBD0DA”.

Info: Removing unused footprint “C104A:/5B870BAA/EA09F549”.

Info: Removing unused footprint “R136A:/5B870BAA/2D5E3D32”.

Info: Removing unused footprint “C109A:/5B870BAA/3C0F6B5D”.

Info: Removing unused footprint “R140A:/5B870BAA/AC78513E”.

Info: Removing unused footprint “K_DOUT:/5B870870/703699AE”.

Info: Removing unused footprint “R65A:/5B86F516/962C63C6”.

Info: Removing unused footprint “R78B:/5B86FCC4/E8D586BE”.

Info: Removing unused footprint “R65B:/5B86F516/43B2D74C”.

Info: Processing component “J7:/5B8722D3/53EFFFD8:EEZ PSU consolidated r5B13a:693072010801”.

Info: Processing component “FB3:/5B86F281/FFBF76DA:EEZ PSU consolidated r5B13a:BEAD0603”.

Info: Processing component “FB4:/5B870870/ABDA1C34:EEZ PSU consolidated r5B13a:BEAD0603”.

Info: Processing component “FB5:/5B870870/1F860F62:EEZ PSU consolidated r5B13a:BEAD0603”.

Info: Processing component “FB6:/5B870870/19FB1623:EEZ PSU consolidated r5B13a:BEAD0603”.

Info: Processing component “FB7:/5B871CD8/7F60FBD0:EEZ PSU consolidated r5B13a:BEAD0603”.

Info: Processing component “FB2:/5B86F281/BFA9910D:EEZ PSU consolidated r5B13a:BEAD0603”.

Info: Processing component “FB1:/5B86F281/BDB48BD5:EEZ PSU consolidated r5B13a:BEAD0603”.

Info: Processing component “MCU1:/5B8711C3/38E59275:EEZ PSU consolidated r5B13a:ARDUINO+ICSP_MIRROR”.

Info: Adding new symbol “MCU1:/5B8711C3/38E59275” footprint “EEZ PSU consolidated r5B13a:ARDUINO+ICSP_MIRROR”.

Info: Processing component “C73:/5B870139/4DA409FC:EEZ PSU consolidated r5B13a:C0603”.

Info: Processing component “X4:/5B870419/38D8100C:EEZ PSU consolidated r5B13a:22-23-2031”.

Info: Processing component “X17:/5B871692/DD509A91:EEZ PSU consolidated r5B13a:22-23-2021”.

Info: Changing copper zone net name from “VSS” to “GND”.
Info: Removing unused footprint “EEZ_SIGNATURE:”.

Info: Removing unused footprint “R78A:/5B86FCC4/BF39F499”.

Info: Removing unused footprint “U$4:”.

Info: Removing unused footprint “U$2:”.

Info: Removing unused footprint “U$3:”.

Info: Removing unused footprint “EEZ_SIGNATURE1:”.

Info: Processing component “C131:/5B871692/136A0F4A:EEZ PSU consolidated r5B13a:C0805”.

Info: Processing component “C18:/5B86EEA2/99C619D6:EEZ PSU consolidated r5B13a:C0805”.

Info: Processing component “C19:/5B86EEA2/9B450B35:EEZ PSU consolidated r5B13a:C0805”.

Info: Processing component “C149:/5B8722D3/9E052CF6:EEZ PSU consolidated r5B13a:C0805”.

Info: Processing component “C92:/5B870BAA/3363AE49:EEZ PSU consolidated r5B13a:C0805”.

Info: Processing component “C25:/5B86F281/8D957147:EEZ PSU consolidated r5B13a:C0805”.

Info: Processing component “C87:/5B870BAA/EEC5F00B:EEZ PSU consolidated r5B13a:C0805”.

Info: Processing component “C26:/5B86F281/A0BF2441:EEZ PSU consolidated r5B13a:C0805”.

Info: Processing component “C120:/5B871692/9DDDB525:EEZ PSU consolidated r5B13a:C0805”.

Info: Processing component “C28:/5B86F281/795FF24F:EEZ PSU consolidated r5B13a:C0805”.

Info: Processing component “C151:/5B8722D3/30CD8390:EEZ PSU consolidated r5B13a:C0805”.

Info: Processing component “C140:/5B871CD8/9DF23C2E:EEZ PSU consolidated r5B13a:C0805”.

Info: Processing component “C14:/5B86EEA2/B8E8E18D:EEZ PSU consolidated r5B13a:C0805”.

Info: Processing component “C58:/5B86FCC4/F82BCFBC:EEZ PSU consolidated r5B13a:C0805”.

Info: Processing component “C37:/5B86F516/130E8044:EEZ PSU consolidated r5B13a:C0805”.

Info: Processing component “C34:/5B86F516/937EAE9D:EEZ PSU consolidated r5B13a:C0805”.

Info: Processing component “C36:/5B86F516/6B0E3443:EEZ PSU consolidated r5B13a:C0805”.

Info: Processing component “C64:/5B86FCC4/DB38927D:EEZ PSU consolidated r5B13a:C0805”.

Info: Processing component “C35:/5B86F516/E3413257:EEZ PSU consolidated r5B13a:C0805”.

Info: Processing component “C66:/5B86FCC4/F5063824:EEZ PSU consolidated r5B13a:C0805”.

Info: Processing component “C156:/5B871CD8/99722CA6:EEZ PSU consolidated r5B13a:C0805”.

Info: Processing component “C2:/5B86EEA2/763BB0C5:EEZ PSU consolidated r5B13a:C1206”.

Info: Processing component “C75:/5B870419/9D2E4EBB:EEZ PSU consolidated r5B13a:C102-064X133”.

Info: Processing component “C104A1:/5B870BAA/EA09F549:EEZ PSU consolidated r5B13a:C0805”.

Info: Adding new symbol “C104A1:/5B870BAA/EA09F549” footprint “EEZ PSU consolidated r5B13a:C0805”.

Info: Processing component “C11:/5B86EEA2/5F67C8AF:EEZ PSU consolidated r5B13a:C0805”.

Info: Processing component “C152:/5B8722D3/F74D0BDE:EEZ PSU consolidated r5B13a:C0805”.

Info: Processing component “C118:/5B871692/4747FEF7:EEZ PSU consolidated r5B13a:C0805”.

Info: Processing component “C153:/5B8722D3/1AACB6B6:EEZ PSU consolidated r5B13a:C0805”.

Info: Processing component “C155:/5B8722D3/29C637D0:EEZ PSU consolidated r5B13a:C0805”.

Info: Processing component “C67:/5B86FCC4/2B3649F3:EEZ PSU consolidated r5B13a:C0805”.

Info: Processing component “C7:/5B86EEA2/541178FC:EEZ PSU consolidated r5B13a:C0805”.

Info: Processing component “C150:/5B8722D3/62F2389B:EEZ PSU consolidated r5B13a:C0805”.

Info: Processing component “C109A1:/5B870BAA/3C0F6B5D:EEZ PSU consolidated r5B13a:C0805”.

Info: Adding new symbol “C109A1:/5B870BAA/3C0F6B5D” footprint “EEZ PSU consolidated r5B13a:C0805”.

Info: Processing component “C115:/5B871692/284AEFDC:EEZ PSU consolidated r5B13a:C0805”.

Info: Processing component “C17:/5B86EEA2/9029B192:EEZ PSU consolidated r5B13a:C0805”.

Info: Processing component “C61:/5B86FCC4/548BE353:EEZ PSU consolidated r5B13a:C0805”.

Info: Processing component “C60:/5B86FCC4/7C8BB522:EEZ PSU consolidated r5B13a:C0805”.

Info: Processing component “C12:/5B86EEA2/DDA156A1:EEZ PSU consolidated r5B13a:C0805”.

Info: Processing component “C44:/5B86F516/80C8C850:EEZ PSU consolidated r5B13a:C0603”.

Info: Processing component “C38:/5B86F516/8087CD94:EEZ PSU consolidated r5B13a:C0805”.

Info: Processing component “C53:/5B86F516/B38B1921:EEZ PSU consolidated r5B13a:C0805”.

Info: Processing component “C76:/5B870419/6A422362:EEZ PSU consolidated r5B13a:C075-052X106”.

Info: Processing component “C111:/5B871692/3A464919:EEZ PSU consolidated r5B13a:C0603”.

Info: Processing component “C113:/5B871692/44F75243:EEZ PSU consolidated r5B13a:C0603”.

Info: Processing component “C114:/5B871692/98E95D18:EEZ PSU consolidated r5B13a:C0603”.

Info: Processing component “C126:/5B871692/31BE1853:EEZ PSU consolidated r5B13a:C0603”.

Info: Processing component “C43:/5B86F516/2129E4BB:EEZ PSU consolidated r5B13a:C0603”.

Info: Processing component “C45:/5B86F516/F1D35E7E:EEZ PSU consolidated r5B13a:C0603”.

Info: Processing component “C39:/5B86F516/B736FEA5:EEZ PSU consolidated r5B13a:C0805”.

Info: Processing component “C50:/5B86F516/BBCE79FA:EEZ PSU consolidated r5B13a:C0603”.

Info: Processing component “C51:/5B86F516/B5FA8829:EEZ PSU consolidated r5B13a:C0603”.

Info: Processing component “C54:/5B86FCC4/7AD5D4FB:EEZ PSU consolidated r5B13a:C0603”.

Info: Processing component “C56:/5B86FCC4/5C8639F4:EEZ PSU consolidated r5B13a:C0603”.

Info: Processing component “C134:/5B871CD8/E49F44B8:EEZ PSU consolidated r5B13a:C0603”.

Info: Processing component “C59:/5B86FCC4/8EF9A0BF:EEZ PSU consolidated r5B13a:C0603”.

Info: Processing component “C63:/5B86FCC4/EC4500C0:EEZ PSU consolidated r5B13a:C0603”.

Info: Processing component “C65:/5B86FCC4/E7D5C9F7:EEZ PSU consolidated r5B13a:C0603”.

Info: Processing component “C69:/5B86FCC4/D3FBB675:EEZ PSU consolidated r5B13a:C0603”.

Info: Processing component “C46:/5B86F516/048D8E5C:EEZ PSU consolidated r5B13a:C0805”.

Info: Processing component “C68:/5B86FCC4/E14F816B:EEZ PSU consolidated r5B13a:C0805”.

Info: Processing component “C62:/5B86FCC4/EABAF55D:EEZ PSU consolidated r5B13a:C0805”.

Info: Processing component “C70:/5B870139/8D45B8A5:EEZ PSU consolidated r5B13a:C0805”.

Info: Processing component “C71:/5B870139/3CEB0D3B:EEZ PSU consolidated r5B13a:C0805”.

Info: Processing component “C138:/5B871CD8/2F5FD116:EEZ PSU consolidated r5B13a:C0805”.

Info: Processing component “C74:/5B870139/0498734A:EEZ PSU consolidated r5B13a:C0805”.

Info: Processing component “C133:/5B871CD8/9F22C80D:EEZ PSU consolidated r5B13a:C0805”.

Info: Processing component “C42:/5B86F516/3486AFA6:EEZ PSU consolidated r5B13a:C0805”.

Info: Processing component “C41:/5B86F516/D382C713:EEZ PSU consolidated r5B13a:C0805”.

Info: Processing component “R31:/5B86F516/139179C0:EEZ PSU consolidated r5B13a:R0805”.

Info: Processing component “C47:/5B86F516/EAD17618:EEZ PSU consolidated r5B13a:C0805”.

Info: Processing component “C48:/5B86F516/2519B722:EEZ PSU consolidated r5B13a:C0805”.

Info: Processing component “C116:/5B871692/A096F6CF:EEZ PSU consolidated r5B13a:C0805”.

Info: Processing component “C40:/5B86F516/326AD41E:EEZ PSU consolidated r5B13a:C0805”.

Info: Processing component “C52:/5B86F516/849D4C53:EEZ PSU consolidated r5B13a:C0805”.

Info: Processing component “C79:/5B870419/A167EEB6:EEZ PSU consolidated r5B13a:C0805”.

Info: Processing component “C137:/5B871CD8/BBA0131D:EEZ PSU consolidated r5B13a:C0805”.

Info: Processing component “C135:/5B871CD8/4367AAA9:EEZ PSU consolidated r5B13a:C0805”.

Info: Processing component “ZD2:/5B86F516/B70FD2B4:EEZ PSU consolidated r5B13a:SOD323-W”.

Info: Processing component “IC17:/5B870870/2B3093F6:EEZ PSU consolidated r5B13a:SOIC-16W”.

Info: Processing component “IC23:/5B8711C3/50C5BD01:EEZ PSU consolidated r5B13a:SOIC-16”.

Info: Processing component “IC21:/5B8711C3/5B393C38:EEZ PSU consolidated r5B13a:SOIC-16”.

Info: Processing component “IC20:/5B8711C3/A6F2FB68:EEZ PSU consolidated r5B13a:SOIC-16”.

Info: Processing component “IC19:/5B8711C3/423C60E2:EEZ PSU consolidated r5B13a:SOIC-16”.

Info: Processing component “D14:/5B870BAA/501335DE:EEZ PSU consolidated r5B13a:SOD323-W”.

Info: Processing component “D18:/5B871692/15D816E0:EEZ PSU consolidated r5B13a:SOD323-W”.

Info: Processing component “D15:/5B870BAA/70ACD835:EEZ PSU consolidated r5B13a:SOD323-W”.

Info: Processing component “D12:/5B870870/CF94C26F:EEZ PSU consolidated r5B13a:SOD323-W”.

Info: Processing component “IC7:/5B86F516/51F87B19:EEZ PSU consolidated r5B13a:SOIC127P600X173-8N”.

Info: Processing component “ZD3:/5B86F516/40047A14:EEZ PSU consolidated r5B13a:SOD323-W”.

Info: Processing component “ZD16:/5B86F281/4178B1DA:EEZ PSU consolidated r5B13a:SOD323-W”.

Info: Processing component “ZD17:/5B870870/84E9DBFB:EEZ PSU consolidated r5B13a:SOD323-W”.

Info: Processing component “D10:/5B86F516/F28DB082:EEZ PSU consolidated r5B13a:SOD323-R”.

Info: Processing component “D8:/5B86F516/2D27320D:EEZ PSU consolidated r5B13a:SOD323-R”.

Info: Processing component “D21:/5B871CD8/CDC926C0:EEZ PSU consolidated r5B13a:SOD323-R”.

Info: Processing component “D7:/5B86F516/6865CB0A:EEZ PSU consolidated r5B13a:SOD323-R”.

Info: Processing component “D6:/5B86F516/F4E8650C:EEZ PSU consolidated r5B13a:SOD323-R”.

Info: Processing component “IC16:/5B870870/C0E1BD3A:EEZ PSU consolidated r5B13a:SOP192P292X122-4N”.

Info: Changing symbol “IC29:/0282EACC” pin “7” net name from “VSS” to “GND”.

Info: Processing component “IC24:/5B871692/460000D5:EEZ PSU consolidated r5B13a:SOP65P640X120-14N”.

Info: Processing component “IC34:/5B8722D3/86424953:EEZ PSU consolidated r5B13a:SOP65P490X110-9N”.

Info: Processing component “IC32:/5B871CD8/DC1EE195:EEZ PSU consolidated r5B13a:SOP65P400X130-8N”.

Info: Changing symbol path “IC32:/60E9AF5F” to “/5B871CD8/DC1EE195”.

Info: Changing symbol “IC32:/60E9AF5F” pin “8” net name from “VDD” to “+3V3”.

Info: Changing symbol “IC32:/60E9AF5F” pin “4” net name from “VSS” to “GND”.

Info: Processing component “IC18:/5B870BAA/6EFA9414:EEZ PSU consolidated r5B13a:SOP63P600X175-24N”.

Info: Processing component “IC4:/5B86F281/3C2C53A5:EEZ PSU consolidated r5B13a:SOP50P490X110-17N”.

Info: Processing component “D5:/5B86F516/D1642B09:EEZ PSU consolidated r5B13a:SOD323-R”.

Info: Processing component “IC31:/5B871CD8/E590BB07:EEZ PSU consolidated r5B13a:SOIC127P600X175-8N”.

Info: Processing component “IC9:/5B86FCC4/41F01822:EEZ PSU consolidated r5B13a:SOIC127P600X175-8N”.

Info: Processing component “IC2:/5B86F281/BC34DC86:EEZ PSU consolidated r5B13a:SOIC127P600X175-8N”.

Info: Processing component “IC25:/5B871692/30602457:EEZ PSU consolidated r5B13a:SOIC127P600X175-8N”.

Info: Processing component “IC28:/5B871CD8/77EB61E3:EEZ PSU consolidated r5B13a:SOIC127P600X175-8N”.

Info: Processing component “IC14:/5B870139/AA6C0E53:EEZ PSU consolidated r5B13a:SOIC127P600X175-14N”.

Info: Processing component “IC6:/5B86F516/2214B29C:EEZ PSU consolidated r5B13a:SOIC127P600X173-8N”.

Info: Processing component “IC5:/5B86F516/C057A724:EEZ PSU consolidated r5B13a:SOIC127P600X173-8N”.

Info: Processing component “R65B1:/5B86F516/43B2D74C:EEZ PSU consolidated r5B13a:R2512”.

Info: Processing component “K_SER1:/5B870BAA/9978EF33:EEZ PSU consolidated r5B13a:RT-C_016A5_ROUND”.

Info: Adding new symbol “K_SER1:/5B870BAA/9978EF33” footprint “EEZ PSU consolidated r5B13a:RT-C_016A5_ROUND”.

Info: Processing component “K_PAR1:/5B870BAA/DEAF6977:EEZ PSU consolidated r5B13a:RT-C_016A5_ROUND”.

Info: Adding new symbol “K_PAR1:/5B870BAA/DEAF6977” footprint “EEZ PSU consolidated r5B13a:RT-C_016A5_ROUND”.

Info: Processing component “K_DOUT1:/5B870870/703699AE:EEZ PSU consolidated r5B13a:RT-C_016A5_ROUND”.

Info: Adding new symbol “K_DOUT1:/5B870870/703699AE” footprint “EEZ PSU consolidated r5B13a:RT-C_016A5_ROUND”.

Info: Processing component “L1:/5B86EEA2/ABFF23E9:EEZ PSU consolidated r5B13a:RN112”.

Info: Processing component “X7:/5B870870/9F533755:EEZ PSU consolidated r5B13a:RJ45-VERT”.

Info: Processing component “Y1:/5B871692/7D89E2D8:EEZ PSU consolidated r5B13a:R26_XTAL”.

Info: Processing component “NTC1:/5B86EEA2/655A7CC6:EEZ PSU consolidated r5B13a:R_0204_5+0805”.

Info: Adding new symbol “R65B1:/5B86F516/43B2D74C” footprint “EEZ PSU consolidated r5B13a:R2512”.

Info: Processing component “R105:/5B870419/2BFC61D2:EEZ PSU consolidated r5B13a:R2512”.

Info: Processing component “R104:/5B870419/150225E3:EEZ PSU consolidated r5B13a:R2512”.

Info: Processing component “R111:/5B870419/0D50473B:EEZ PSU consolidated r5B13a:R2512”.

Info: Processing component “R65:/5B86F516/369965EA:EEZ PSU consolidated r5B13a:R2512”.

Info: Processing component “R4:/5B86EEA2/3351D600:EEZ PSU consolidated r5B13a:R2512”.

Info: Processing component “R26:/5B86F516/4668C9E6:EEZ PSU consolidated r5B13a:R2512”.

Info: Processing component “R108:/5B870419/AE52F84A:EEZ PSU consolidated r5B13a:R2512”.

Info: Processing component “R78B1:/5B86FCC4/E8D586BE:EEZ PSU consolidated r5B13a:R0805”.

Info: Processing component “D4:/5B86F516/7DD77E9D:EEZ PSU consolidated r5B13a:SOD323-R”.

Info: Processing component “D3:/5B86F516/EA1F28D5:EEZ PSU consolidated r5B13a:SOD323-R”.

Info: Processing component “D9:/5B86F516/B81038A9:EEZ PSU consolidated r5B13a:SOD323-R”.

Info: Processing component “D16:/5B870BAA/33277A18:EEZ PSU consolidated r5B13a:SOD323-R”.

Info: Processing component “D13:/5B870BAA/9C4A1539:EEZ PSU consolidated r5B13a:SOD323-R”.

Info: Processing component “D2:/5B86EEA2/753AA296:EEZ PSU consolidated r5B13a:SOD323-R”.

Info: Processing component “D20:/5B871CD8/553A3D11:EEZ PSU consolidated r5B13a:SOD123”.

Info: Processing component “D11:/5B870419/A4285309:EEZ PSU consolidated r5B13a:SOD123”.

Info: Changing symbol “IC29:/0282EACC” pin “14” net name from “VDD” to “+3V3”.

Info: Processing component “SH1:/5B86EEA2/10015477:EEZ PSU consolidated r5B13a:SHORT_NOHOLE”.

Info: Processing component “SH2:/5B86EEA2/5ABD8682:EEZ PSU consolidated r5B13a:SHORT_NOHOLE”.

Info: Processing component “SH3:/5B871692/CD25553D:EEZ PSU consolidated r5B13a:SHORT_NOHOLE”.

Info: Processing component “C112:/5B871692/430E7ECC:EEZ PSU consolidated r5B13a:SG-R20MM”.

Info: Processing component “SAR1:/5B870419/BDD41D1A:EEZ PSU consolidated r5B13a:SAR”.

Info: Processing component “R65A1:/5B86F516/962C63C6:EEZ PSU consolidated r5B13a:R_2512-4WIRE”.

Info: Adding new symbol “R65A1:/5B86F516/962C63C6” footprint “EEZ PSU consolidated r5B13a:R_2512-4WIRE”.

Info: Processing component “R103:/5B870419/065D7068:EEZ PSU consolidated r5B13a:R_0913”.

Info: Processing component “Q14:/5B86F516/474C9E1C:EEZ PSU consolidated r5B13a:TO229P990X239-3N”.

Info: Processing component “Q21:/5B870419/9E148865:EEZ PSU consolidated r5B13a:TOP3S-1”.

Info: Processing component “IC3:/5B86F281/E7B5215D:EEZ PSU consolidated r5B13a:TO254P1524X483-4N”.

Info: Processing component “D22:/5B8722D3/E1EBF7A8:EEZ PSU consolidated r5B13a:TO252”.

Info: Processing component “D1:/5B86EEA2/6183C455:EEZ PSU consolidated r5B13a:TO252”.

Info: Processing component “D23:/5B8722D3/F5BC6505:EEZ PSU consolidated r5B13a:TO252”.

Info: Processing component “D24:/5B8722D3/79C94C35:EEZ PSU consolidated r5B13a:TO252”.

Info: Processing component “D25:/5B8722D3/4F6036A1:EEZ PSU consolidated r5B13a:TO252”.

Info: Processing component “Q4:/5B86F516/F2A595F1:EEZ PSU consolidated r5B13a:TO247BH-CLR”.

Info: Processing component “Q7:/5B86F516/7C787F1D:EEZ PSU consolidated r5B13a:TO229P990X239-3N”.

Info: Processing component “Q22:/5B870419/39112899:EEZ PSU consolidated r5B13a:TOP3S-1”.

Info: Processing component “Q1:/5B86EEA2/34F7D08B:EEZ PSU consolidated r5B13a:TO229P990X239-3N”.

Info: Processing component “X19:/5B8722D3/E00AC1C7:EEZ PSU consolidated r5B13a:TBLOCK5.0_2”.

Info: Processing component “SW3:/5B871CD8/AADFE4DD:EEZ PSU consolidated r5B13a:TACTM-6XN”.

Info: Processing component “X2:/5B86EEA2/EE6A8C1F:EEZ PSU consolidated r5B13a:SSW-113-02-T-D-RA”.

Info: Processing component “X10:/5B870870/65FD905D:EEZ PSU consolidated r5B13a:SSW-105-02-S-S”.

Info: Processing component “X9:/5B870870/E9081463:EEZ PSU consolidated r5B13a:SSW-105-02-S-S”.

Info: Processing component “IC30:/5B871CD8/A7DF8CAF:EEZ PSU consolidated r5B13a:SOT95P280X145-5N”.

Info: Processing component “Q26:/5B870BAA/45FD1AB3:EEZ PSU consolidated r5B13a:SOT95P237X112-3N”.

Info: Changing symbol “VAR4:/5B870870/A5CDC9AD” pin “1” net name from “Net-(K_DOUT-Pad11A)” to “Net-(K_DOUT1-Pad11A)”.

Info: Processing component “JP9:/5B870870/6D2E4931:EEZ PSU consolidated r5B13a:ZL303-03P”.

Info: Processing component “X6:/5B870870/8EB02048:EEZ PSU consolidated r5B13a:WR-TBL_3-PIN”.

Info: Changing symbol “X6:/5B870870/8EB02048” pin “3” net name from “Net-(K_DOUT-Pad12A)” to “Net-(K_DOUT1-Pad12A)”.

Info: Changing symbol “X6:/5B870870/8EB02048” pin “2” net name from “Net-(K_DOUT-Pad11A)” to “Net-(K_DOUT1-Pad11A)”.

Info: Changing symbol “X6:/5B870870/8EB02048” pin “1” net name from “Net-(K_DOUT-Pad14A)” to “Net-(K_DOUT1-Pad14A)”.

Info: Processing component “L2:/5B86EEA2/0840620C:EEZ PSU consolidated r5B13a:WE-HCI_1350_1365”.

Info: Processing component “VAR4:/5B870870/A5CDC9AD:EEZ PSU consolidated r5B13a:VARISTOR_13MM”.

Info: Changing symbol “VAR4:/5B870870/A5CDC9AD” pin “2” net name from “Net-(K_DOUT-Pad12A)” to “Net-(K_DOUT1-Pad12A)”.

Info: Processing component “Q29:/5B870BAA/F121C6CA:EEZ PSU consolidated r5B13a:SOT95P237X112-3N”.

Info: Processing component “VAR3:/5B870870/E3CA4E1E:EEZ PSU consolidated r5B13a:VARISTOR_13MM”.

Info: Changing symbol “VAR3:/5B870870/E3CA4E1E” pin “2” net name from “Net-(K_DOUT-Pad14A)” to “Net-(K_DOUT1-Pad14A)”.

Info: Changing symbol “VAR3:/5B870870/E3CA4E1E” pin “1” net name from “Net-(K_DOUT-Pad11A)” to “Net-(K_DOUT1-Pad11A)”.

Info: Processing component “VAR2:/5B870419/936BA615:EEZ PSU consolidated r5B13a:VARISTOR”.

Info: Processing component “VAR1:/5B870419/E8A8B8EF:EEZ PSU consolidated r5B13a:VARISTOR”.

Info: Processing component “X13:/5B870BAA/89F53A46:EEZ PSU consolidated r5B13a:TSW-113-07-F-D”.

Info: Processing component “X15:/5B870BAA/A188A0E9:EEZ PSU consolidated r5B13a:TSW-113-07-F-D”.

Info: Processing component “IC26:/5B871692/694A8893:EEZ PSU consolidated r5B13a:TQFP48-7X7”.

Info: Processing component “Q25:/5B870870/2176B837:EEZ PSU consolidated r5B13a:SOT103P240X110-3N”.

Info: Processing component “Q10:/5B86F516/8C0DD2A6:EEZ PSU consolidated r5B13a:SOT23-BEC”.

Info: Processing component “D19:/5B871CD8/4E22A259:EEZ PSU consolidated r5B13a:SOT23”.

Info: Processing component “ZD18:/5B86FCC4/2453FF74:EEZ PSU consolidated r5B13a:SOT23”.

Info: Processing component “Q23:/5B870419/C50B955C:EEZ PSU consolidated r5B13a:SOT223”.

Info: Processing component “Q13:/5B86F516/D98636D8:EEZ PSU consolidated r5B13a:SOT223”.

Info: Processing component “IC22:/5B8711C3/7EAF38F5:EEZ PSU consolidated r5B13a:SOT223”.

Info: Processing component “Q3:/5B86EEA2/9A1C1EBA:EEZ PSU consolidated r5B13a:SOT103P240X110-3N”.

Info: Processing component “Q16:/5B86FCC4/B7871434:EEZ PSU consolidated r5B13a:SOT103P240X110-3N”.

Info: Processing component “Q30:/5B871692/DEDA13F4:EEZ PSU consolidated r5B13a:SOT103P240X110-3N”.

Info: Processing component “Q9:/5B86F516/8519C255:EEZ PSU consolidated r5B13a:SOT23-BEC”.

Info: Changing symbol “Q25:/5B870870/2176B837” pin “3” net name from “Net-(K_DOUT-PadA2)” to “Net-(K_DOUT1-PadA2)”.

Info: Processing component “Q33:/5B871CD8/2F939DB1:EEZ PSU consolidated r5B13a:SOT103P240X110-3N”.

Info: Processing component “Q34:/5B86F516/8F8BCDB3:EEZ PSU consolidated r5B13a:SOT103P240X110-3N”.

Info: Processing component “Q24:/5B870419/C1C09424:EEZ PSU consolidated r5B13a:SOT103P240X110-3N”.

Info: Processing component “Q32:/5B871CD8/CA0EE761:EEZ PSU consolidated r5B13a:SOT103P240X110-3N”.

Info: Processing component “IC8:/5B86FCC4/D5CFED59:EEZ PSU consolidated r5B13a:SOP65P780X200-28N”.

Info: Processing component “IC29:/5B871CD8/84F2BA6A:EEZ PSU consolidated r5B13a:SOP65P640X120-14N”.

Info: Changing symbol path “IC29:/0282EACC” to “/5B871CD8/84F2BA6A”.

Info: Processing component “Q6:/5B86F516/EA9AFBF2:EEZ PSU consolidated r5B13a:SOT230P700X180-4N”.

Info: Processing component “Q28:/5B870BAA/806F67F3:EEZ PSU consolidated r5B13a:SOT95P237X112-3N”.

Info: Processing component “Q27:/5B870BAA/9F2D8CC0:EEZ PSU consolidated r5B13a:SOT95P237X112-3N”.

Info: Processing component “Q31:/5B871692/93F5E937:EEZ PSU consolidated r5B13a:SOT95P237X112-3N”.

Info: Processing component “Q15:/5B86FCC4/F0AAECAC:EEZ PSU consolidated r5B13a:SOT95P237X112-3N”.

Info: Processing component “IC12:/5B86FCC4/F20560FD:EEZ PSU consolidated r5B13a:SOT65P210X110-6N”.
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

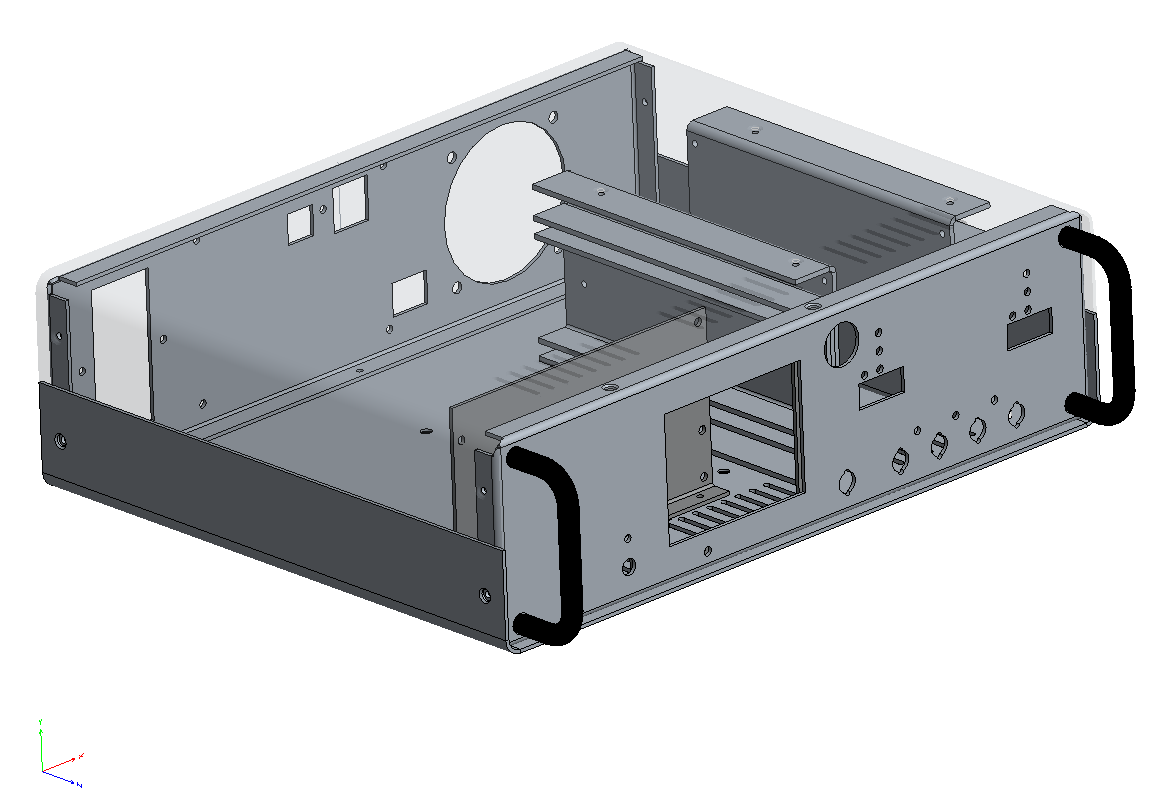
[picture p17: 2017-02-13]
Mechanical/EEZ PSU H24005 enclosure (front view).png

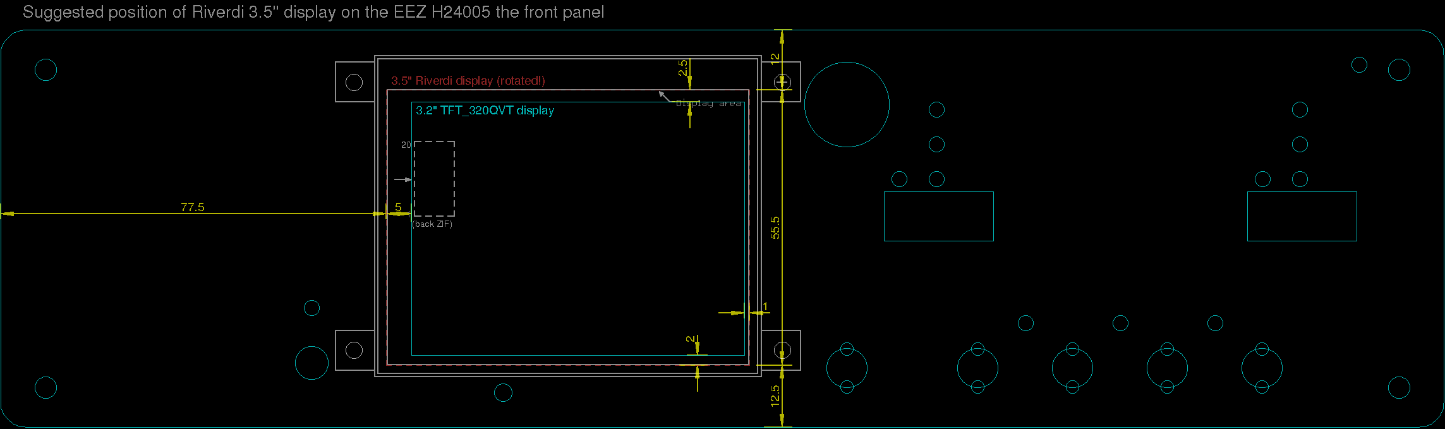
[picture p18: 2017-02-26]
Mechanical/EEZ PSU H24005 dual display hole.png

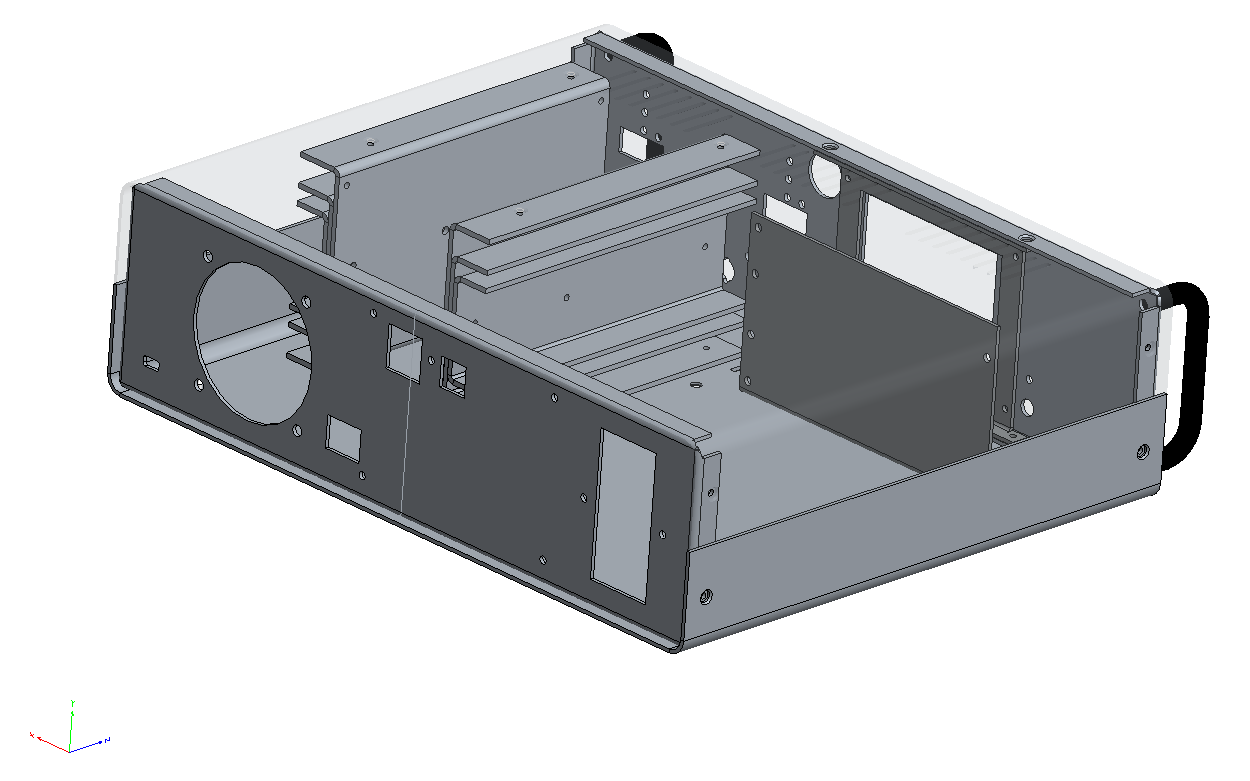
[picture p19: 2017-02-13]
Mechanical/EEZ PSU H24005 enclosure (rear view).png

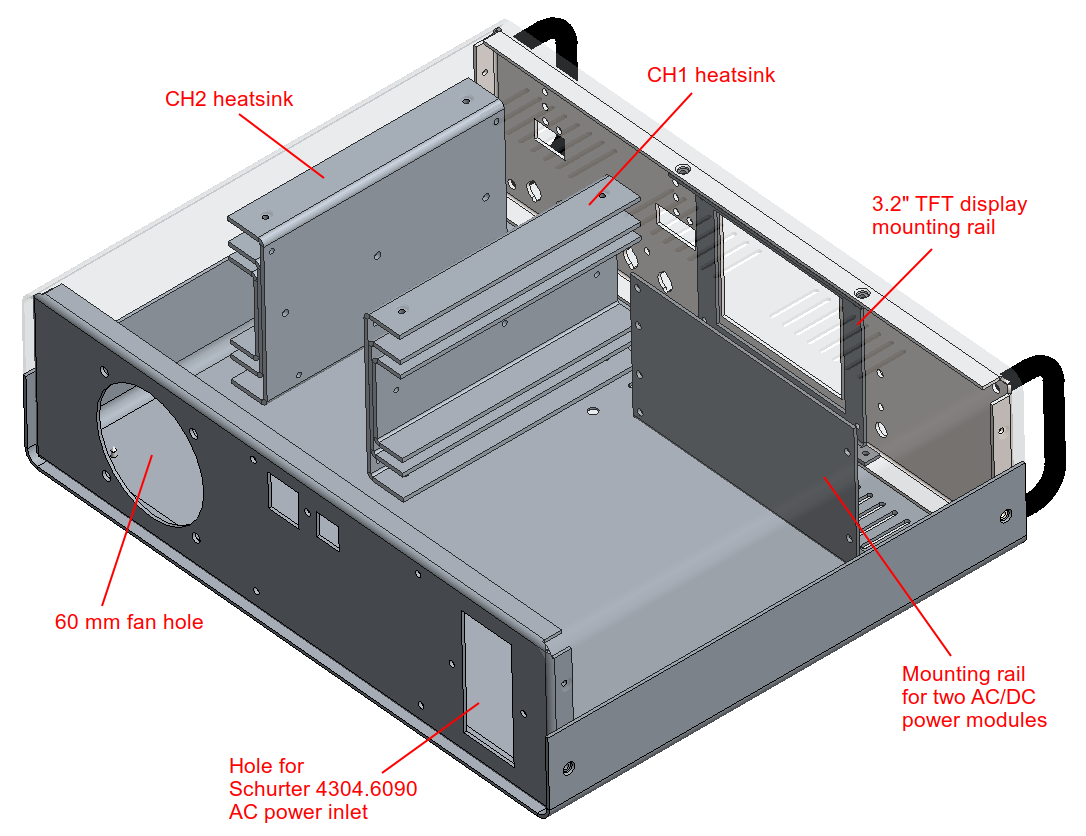
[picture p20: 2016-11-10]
Mechanical/EEZ PSU H24005 Enclosure elements.png

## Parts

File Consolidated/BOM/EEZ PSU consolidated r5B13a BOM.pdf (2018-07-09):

EEZ PSU H24005 BOM (r5B13a, 2018-07-09) Project source code at https://github.com/eez-open
| | | | | | | Farnell / Element14 | | Digi-Key | | Mouser
Qty | Part name | Package | Reference designator | Board name
| | | | | Qty
Code | Part Number | MOQ | Part Number | MOQ | Part Number | MOQ
1 | 1 2x3-pin socket | THT; 2x3-pin socket | MCU-ICSP | Arduino Shield | 1 | 7991983 | M20-7830346 | 1,210 10 | M20-7830346 | 1,000 | M20-7830346 | 0,940
2 | 17 100n 16V X7R | 0603 | | Power board | 34
| 5 100n 16V X7R | 0603 | C81, C82, C83, C84, C85 | AUX PS | 5
27 100n 16V X7R 0603 C97, C98, C99, C100, C101, Arduino Shield 27 C102, C104, C106, C107, C108, C109, C111, C113, C114, C121, C122, C123, C124, C125, C126, C127, C128, C132, C134, C136, C139, C141
| 0603YC104KAT2 A | 06033C104K4T4 A
66 | 2496832 | 0603B104K160CT | 0,012 10 | 0,010 | 0,025
3 | 1 220u 16V | SMD ELCO; Ø6.3 x 7.7mm | C78 | AUX PS | 1 | 1870605 | 0,213 10 | 399-6679-1-ND | 0,410 | 1 | 0,407 | 1
4 | 5 10n 50V X7R | 0805 | C118, C131, C135, C137, C138 | Arduino Shield | 5
| 8 10n 50V X7R | 0805 | | Power board | 16
| | | | | 21 | 1759246 | 0,009 10 | | 0,027 | | 0,014
5 | 2 10u 50V X7R | 1210 | C90, C110 | Arduino Shield | 2
7 10u 50V X7R | 1210 | Power board | 14
16 | 2362133 | 0,748 | 1 | 0,335 | 0,376
6 | 2 10u 10V | 1206, Tantalum | C105, C129 | Arduino Shield | 2
2 10u 10V | 1206, Tantalum | C23, C31 | Power board | 4
6 | 1457413 | T491A106K010AT | 0,260 | 5 | 0,340 | 0,344
7 | 2 120p 50V NP0 | 0805 / 0603 | C17, C39 | Power board | 4 | 1414667 | 0,044 10 | 0,058 | 0,031
8 | 2 18p 50V NP0 | 0805 / 0603 | C116, C120 | Arduino Shield | 2 | 2320820 | 0,026 10 | 0,090 | 0,100
9 | 2 1n 50V NP0 | 0805 / 0603 | C52, C53 | Power board | 4 | 1759227 | 0,029 10 | 0,065 | 0,038
10 | 2 1u 100V X7R | 1206, 100V | C8, C33 | Power board | 4 | 2320876 | 0,200 | 5 | 0,253 | 0,227
11 | 7 1u 50V X7R | 0805, 50V | | Power board | 14
| 1 1u 50V X7R | 0805, 50V | C156 | Arduino board | 1
| | | | | 15 | 2118131 | 0,215 | 5 | 0,129 | 0,135
12 | 1 22n 50V X7R | 0805 | C115 | Arduino Shield | 1 | 1759252 | 0,016 10 | 0,058 | 0,031
13 | 5 2n2 50V NP0 | 0805 / 0603 | C36, C37, C38, C40, C71 | Power board | 10 | 1759236 | 0,052 10 | 0,078 | 0,076

Unit price
€

Unit price
€

Unit price
€

C9, C20, C32, C43, C44, C45, C49, C50, C51, C54, C56, C59, C63, C65, C69, C72, C73

MCESL16V227M6.
3X7.7

80-
EDK227M016A9
HAA

C25, C28, C35, C42, C47, C62, C70, C74
MC0805B103K500
CT

CL21B103KBCN
NNC

GRM216R71H10
3KA01D

C10, C16, C22, C24, C29, C30, C55
GRM32ER71H106
KA12L

CL32B106KBJN
NWE

GRM32ER71H10
6KA12L

T491A106K010A
T

T491A106K010A
T
| C0805C121J5GAC TU | CL21C121JBAN NNC | C0805C121J5GA CTU
| MC0805N180J101 CT | CL21C180JBAN NNC | C0805C180J5GA CTU
| MC0805N102J500 CT | CL21C102JBCN NNC | C0805C102J5GA CTU
| MC1206B105K101 CT | CL31B105KCHN NNE | GRM31CR72A10 5KA01L

C11, C26, C46, C48, C58, C64, C66

C0805C105K5RAC
TU

CL21B105KBFN
NNE

08055C105K4T2
A

MC0805B223K500
CT

CL21B223KBAN
NNC

C0805C223K5R
AC
MC0805N222J500
CT

CL21C222JBFN
NNG

GRM2165C1H22
2JA01D

Qty Part name | RS Components | TME | | Price calculation for 1 set
Unit price Code Part Number MOQ € | Unit price Code / Part Number MOQ € | THT SMD | Lowest Best Order unit price Supplier Qty € | Line Cost €

1 1 2x3-pin socket
2 17 100n 16V X7R

5 100n 16V X7R
27 100n 16V X7R

3 1 220u 16V

4 5 10n 50V X7R
8 10n 50V X7R

5 2 10u 50V X7R
7 10u 50V X7R

6 2 10u 10V
2 10u 10V

7 2 120p 50V NP0

8 2 18p 50V NP0

9 2 1n 50V NP0

10 2 1u 100V X7R

11 7 1u 50V X7R

1 1u 50V X7R

12 1 22n 50V X7R

13 5 2n2 50V NP0

681-6832 M20-7830346 | 0,899 | 5 | ZL262-6DG | 0,070 10 | 1 | TME | 0,070 € | 1 | 0,070
391-246 | 0,004 50 | CL10B104KO8NNNC | 0,004 100 | 66 | RS | 0,004 € 100 | 0,400
839-1770 865080345012 | 0,280 10 | SC1C227M6L07KVR | 0,061 10 | 1 | TME | 0,061 € | 1 | 0,061
461-4013 | 0,007 50 | CL21B103JBANNNC | 0,006 100 | 21 | TME | 0,006 € 20 | 0,120
766-1214 | 0,601 10 | CL32B106KBJNNNE | 0,201 10 | 16 | TME | 0,201 € 16 | 3,216
538-2278 | 0,196 10 | T491A106K010AT | 0,085 10 | 6 | TME | 0,085 € 10 | 0,845
723-6209 | 0,035 100 | CL21C121JBANNNP | 0,007 100 | 4 | TME | 0,007 € 10 | 0,069
648-0935 | 0,157 10 | CL21C180JBANNNC | 0,071 100 | 2 | Farnell | 0,026 € | 2 | 0,053
378-710 0805CG102J9B 0,021 25 B | CL21C102JBCNNNC 0,010 100 | 4 | TME 0,010 € 10 | 0,097
| GRM31CR72A105KA0 1L
740-7590 | 0,174 10 | 0,128 10 | 4 | TME | 0,128 € 10 | 1,279
766-1062 | 0,041 100 | CL21B105KBFNNNG | 0,014 100 | 15 | TME | 0,014 € 15 | 0,214
464-6701 | 0,015 50 | CL21B223KBANNNC | 0,008 100 | 1 | TME | 0,008 € 10 | 0,084
802-9905 | 0,043 100 | | 0,015 100 | 10 | TME | 0,015 € 10 | 0,145

0603YC104JAT2
A

CC0805KRX7R9
BB103

CL32B106KBJN
NNE

T491A106K010A
T

GRM2165C1H1
21JA01D
C0805C180J5G
ACTU

C3216X7R2A10
5K160AA

CL21B105KBFN
NNF

08055C223KAT
2A
C0805C222J5G
ACTU

GRM2165C1H222JA0
1D

Qty Part name Package Reference designator Board name | Code Part Number MOQ € | Part Number Unit price MOQ € | Part Number Unit price MOQ Unit price €
| | | 647-UWT1H220MCL6 GS
| MC0805B332K101 CT | CL21B332KBAN NNC | C0805C332K5R AC
14 | 2 22u 50V | SMD ELCO; Ø8x10.2mm | C89, C94 | Arduino board | 2 | 2326151 | EEE1HA220WAP | 0,341 | 1 | 493-9884-1-ND | 0,280 | 1 | 0,339 | 1
15 | 4 3n3 50V X7R or NP0 | 0805 / 0603 | C60, C61, C67, C68 | Power board | 8 | 1759291 | 0,015 10 | 0,045 | 0,024
16 | 1 470n 50V X7R | 0805, 50V | C7 | Power board | 2
| 2 470n 50V X7R | 0805, 50V | C87, C92 | Arduino Shield | 2
| | | | | 4 | 2470492 | | 0,163 | 5 | | 0,139 | | 0,103
17 | 2 470p 50V NP0 | 0805 / 0603 | C14, C19 | Power board | 4 | 1759217 | 0,023 10 | 0,090 | 0,091
18 | 2 47n 50V X7R | 0805 | C133, C140 | Arduino Shield | 2
1 47n 50V X7R 0805 C79 AUX PS 1
| CL21B473KBCN NNC | 08055C473KAT2 A
3 | 2496983 | 0805B473K500CT | 0,023 10 | 0,090 | 0,091
19 | 1 47n 400V Polyester Film THT R=7,5mm | C76 | AUX PS | 1 | 2468839 | B32520E6473K000 | 0,358 | 1 | - | -
20 | 2 47p 50V NP0 | 0805 / 0603 | C34, C41 | Power board | 4 | 1414692 | 0,028 10 | 0,043 | 0,029
21 | 1 47u 35V | SMD ELCO, Ø6.3 x 5.8mm | C103 | Arduino Shield | 1 | 9695850 | EEEFK1V470P | 0,493 | 1 | EEEFK1V470P | 0,440 | EEEFK1V470P | 0,443
22 | 1 47u 50V | SMD ELCO; Ø8x10.2mm | C13 | Power board | 2 | 9695931 | EEEFK1H470P | 0,622 | 1 | PCE3815CT-ND | 0,600 | 1 | 0,754 | 1
23 | 4 | 0805 | C1, C2, C4, C18 | Power board | 8
4 4n7 100V X7R 0805 C88, C91, C93, C95 Arduino board 4
| MC0805B472K101 CT | CL21B472KCAN NNC | GRM21AR72D47 2KW01D
12 | 1759293 | 0,019 10 | 0,065 | 0,050
24 | 1 4u7 10V | 1206, Tantalum | C130 | Arduino Shield | 1
2 4u7 10V 1206, Tantalum C21, C57 Power board 4
| T491A475K010A T | T491A475K010A T
5 | 1457428 | T491A475K016AT | 0,238 | 5 | 0,310 | 0,299
25 | 2 4u7 100V X7R | 1210, 100V, X7R | C5, C6 | Power board | 4 | 2211140 | | 1,560 | 1 | | 1,240 | | 1,250
26 | 2 6n8 50V X7R or NP0 | 0603 | C117, C119 | Arduino Shield | 2 | 1759100 | 0,007 10 | 0,090 | 0,091
27 | 1 | THT R=10mm | C75 | AUX PS | 1 | 2478385 | R413F16804000M | 0,528 | 1 | | 0,520 | | 0,525
28 | 1 1F 5,5V Backup Cap | THT | C112 | Arduino Shield | 1 | 9697497 | EEC-S5R5H105 | 4,660 | 1 | EEC-S5R5H105 | 3,480 | EEC-S5R5H105 | 3,510
29 | 1 100u 63V | SMD ELCO; Ø10 x 10.2mm | C15 | Power board | 2 | 9696040 | EEEFK1J101P | 0,846 | 1 | EEE-FK1J101P | 0,930 | EEE-FK1J101P | 0,932
30 | 2 18u 50V | | | Power bord | 2
| 2 18u 50V | | C86, C96 | Arduino Shield | 2
4 | 2354813 | 50SVPF18M | 1,830 | 1 | P18942CT-ND | 1,430 | 1 | 667-50SVPF18M | 1,720 | 1
31 | 1 BAS316 | SOD-323 | D12 | AUX PS | 1
| 6 BAS316 | SOD-323 | D13, D14, D15, D16, D18, D21 | Arduino Shield | 6

GRM21BR71H474
KA88L

CL21B474KBFN
FNE

C0805C474K5R
ACTU

MC0805N471J500
CT

CL21C471JBAN
NNC

08055A471JAT2
A

C0805C470J5GAC
TU

CL21C470JBAN
NNC

C0805C470J5GA
CTU

667-EEE-FK1H470P
4n7 100V X7R
CGA6M3X7S2A47 5K200AB | GRJ32DC72A47 5KE11L | GRJ32DC72A47 5KE11L
| MC0603B682K500 CT | CL10B682KB8N NNC | GRM188R71H68 2KA01J
| | R413F16804000 M | R413F16804000 M

6n8 (X1 / Y2) PP Film
300Vac 1000Vdc

SMD ELCO Polymer;
Ø8x6.9mm

C3

SMD ELCO Polymer;
Ø8x6.9mm

Qty Part name

14 2 22u 50V

15 4 3n3 50V X7R or NP0

16 1 470n 50V X7R
2 470n 50V X7R

17 2 470p 50V NP0

18 2 47n 50V X7R
1 47n 50V X7R

19 1 47n 400V Polyester Film

20 2 47p 50V NP0

21 1 47u 35V
22 1 47u 50V

23 4
4

24 1 4u7 10V
2 4u7 10V

25 2 4u7 100V X7R

26 2 6n8 50V X7R or NP0

27 1

28 1 1F 5,5V Backup Cap
29 1 100u 63V
30 2 18u 50V

2 18u 50V

31 1 BAS316
6 BAS316

4n7 100V X7R
4n7 100V X7R

6n8 (X1 / Y2) PP Film
300Vac 1000Vdc
Code Part Number MOQ € | Code / Part Number Unit price MOQ € | THT SMD | Best Order unit price Supplier Qty € | Line Cost € Unit price
| 520-2009 UWT1H220MCL 0,174 25 1GB | UWT1H220MCL6GS 0,009 10 | 2 | TME 0,009 € 5 | 0,047
237-7009 | 0,038 50 | CL21B332KBANNNC | 0,007 100 | 8 | TME | 0,007 € 10 | 0,069
766-1053 | 0,085 50 | CL21B474KBFNNNG | 0,015 100 | 4 | TME | 0,015 € 10 | 0,153
378-700 | 0,021 25 | CL21C471JBANNNC | 0,009 100 | 4 | TME | 0,009 € | 2 | 0,018
391-303 | 0,011 50 | CC0805KRX7R9473 | 0,008 100 | 3 | TME | 0,008 € | 3 | 0,025
668-9993 | 0,241 10 | - | 1 | RS | 0,241 € | 1 | 0,241
264-4270 | 0,014 25 | CC0805JRNPO9470 | 0,007 100 | 4 | TME | 0,007 € 10 | 0,074
565-623 | EEEFK1V470AP | 0,165 | 5 | EEEFK1V470P | 0,157 | 5 | 1 | TME | 0,157 € 10 | 1,572
537-0590 EEEFK1H470P | 0,170 | 5 | EEEFK1H470P | 0,197 | 5 | 2 | RS | 0,170 € | 5 | 0,850
698-3364 | 0,036 25 | CL21B472KCANNNC | 0,006 100 | 12 | TME | 0,006 € 20 | 0,126
538-2341 | 0,179 10 | T491A475M010AT | 0,128 | 5 | 5 | TME | 0,128 € | 5 | 0,640
915-5415 | 0,686 | 5 | - | | | 4 | RS | 0,686 € | 4 | 2,744
147-825 | 0,007 50 | CL10B682JB8NNNC | 0,004 100 | 2 | TME | 0,004 € 10 | 0,042
871-2489 | 0,420 10 | MKP-Y2-6N8 | 0,158 | 5 | 1 | TME | 0,158 € | 1 | 0,158
339-6843 EECS5R5H105 | 3,556 | 1 | EECS5R5H105 | 2,190 | 1 | 1 | TME | 2,190 € | 1 | 2,190
708-3623 EEEFK1J101P | 0,641 | 5 | EEEFK1J101P | 0,380 | 5 | 2 | TME | 0,380 € | 2 | 0,760
- | - | 4 | Digikey | 1,430 € | 5 | 7,150

GRM216R71H3
32KA01D

CL21B474KBF4
PNG

0805CG471J9B
B

08055C473KAT
2A

B32520C6473K1
89
C0805C470J5G
ACTU

08051C472KAZ
2A

T491A475K016A
T

CGA6M3X7S2A
475K200AB
C0603C682K5R
ACTU
890334023003C
S

Qty Part name Package Reference designator Board name | Code Part Number MOQ € | Part Number Unit price MOQ € | Part Number Unit price MOQ Unit price €

9 BAS316 SOD-323 D2, D3, D4, D5, D6, D7, D8, D9, Power board 18 D10

25 | 8734275 | BAS316,115 | 0,192 | 5 | BAS316,115 | 0,175 | BAS316,115 | 0,174
32 | 1 BAT54S | SOT-23 | D19 | Arduino Shield | 1 | 1621835 | BAT54S | 0,125 10 | BAT54SLT1G | 0,150 | BAT54SLT1G | 0,145
33 | 1 SKL16 | SOD-123F | D11 | AUX PS | 1
| 1 SKL16 | SOD-123F | D20 | Arduino Shield | 1
2 | 1510688 | PMEG4005EH | 0,091 | 5 | 1727-3876-1-ND | 0,430 | 1 | 0,405 | 1
34 | 1 STPS15H100 | TO-252 | D1 | Power board | 2 | 2344052 | | 1,070 | 1 | STPS15H100CB | 0,900 | | STPS15H100CB | 0,896
35 | 1 50mA, polyfuse | 1210 | F1 | Arduino board | 1 | 1861176 | MC36203 | 0,163 | 5 | 507-1476-1-ND | 0,200 | 1 | | 0,101 | 1
36 | 3 60R@100MHz | 0603 Ferrite Bead | FB1, FB2, FB3 | Power board | 6
| 3 60R@100MHz | 0603 Ferrite Bead | FB4, FB5, FB6 | AUX PS | 3
| 1 60R@100MHz | 0603 Ferrite Bead | FB7 | Arduino Shield | 1
| | | | | 10 | 1635704 | 742792602 | 0,210 | 1 | 742792602 | 0,210 | | 742792602 | 0,160
37 | 1 LTC3864EMSE#PBF | MSOP-12 | IC1 | Power board | 2 | 2293128 | | 4,520 | 1 | | 3,960 | | -
38 | 1 DAC8552IDGKTG4 | MSOP-8 (VSSOP-8) | IC10 | Power board | 2 | 1329584 | DAC8552IDGKTG4 | 6,420 | 1 | DAC8552IDGKT | 7,660 | | DAC8552IDGKR | 6,510
39 | 1 TS5A9411DCKT | SC-70 | IC12 | Power board | 2 | 1755582 | TS5A9411DCKT | 1,050 | 1 | TS5A9411DCKR | 0,560 | | TS5A9411DCKR | 0,534
40 | 1 ADS1120IPWR | TSSOP-16 | IC13 | Power board | 2 | 2402249 | ADS1120IPWR | 6,760 | 1 | ADS1120IPWR | 6,250 | | ADS1120IPWR | 6,100
41 | 1 LP339D | SOIC-14 | IC14 | Power board | 2 | 9589686 | LP339D | 0,573 | 1 | LP339DR | 0,520 | | LP339DR | 0,498
42 | 1 TPD4E002DRLR | | IC15 | AUX PS | 1 | 1755329 | TPD4E002DRLR | 0,275 | 1 | 296-21694-1-ND | 0,660 | 1 | | 0,594 | 1
43 | 1 TPD2E001DZDR | | IC16 | AUX PS | 1 | 2335446 | TPD2E001DZDR | 0,506 | 1 | 296-24770-1-ND | 0,580 | 1 | | 0,519 | 1
44 | 1 ADUM3160BRWZ | | IC17 | AUX PS | 1 | 1843660 | ADUM3160BRWZ | 7,070 | 1 | | 7,290 | 1 | | 6,660 | 1
45 | 1 TLC5925IDBQR | SSOP-24 | IC18 | Arduino Shield | 1 | 1694438 | TLC5925IDBQR | 1,520 | 1 | TLC5925IDBQR | 1,370 | | TLC5925IDBQR | 1,330
46 | 2 Si8641EC-B-IS1 | SOIC-16 | IC19, IC23 | Arduino Shield | 2 | 2423294 | Si8641EC-B-IS1 | 3,210 | 1 | Si8641EC-B-IS1 | 2,780 | | Si8641EC-B-IS1 | 2,720
47 | 1 LP2951D | SOIC-8 | IC2 | Power board | 2 | 1755066 | LP2951D | 0,573 | 1 | LP2951DR | 0,520 | | LP2951DR | 0,498
48 | 2 SI8651EC-B-IS1 | SOIC-16 | IC20, IC21 | Arduino Shield | 2 | 2423323 | SI8651EC-B-IS1 | 3,150 | 1 | SI8651EC-B-IS1 | 3,190 | | SI8651EC-B-IS1 | 3,060
49 | 1 LD1117S33TR | TO-252 | IC22 | Arduino Shield | 1 | 1202826 | LD1117S33TR | 0,187 | 5 | 497-1242-1-ND | 0,400 | 1 | 511-LD1117S33 | 0,403 | 1
50 | 1 PCA21125T/Q900/1,1 | TSSOP-14 | IC24 | Arduino Shield | 1 | 2400445 | | 1,870 | 1 | | 1,610 | | | 1,660
51 | 1 AT25256B | SOIC-8 | IC25 | Arduino Shield | 1 | 1841577 | AT25256B-SSHL-B | 1,190 | 1 | | 1,300 | | | 1,290
52 | 1 W5500 | LQFP-48 | IC26 | Arduino Shield | 1 | - | | | | W5500 | 3,750 | | W5500 | 2,390
53 | 1 BC857BS | SOT-363 | IC27 | Arduino Shield | 1 | 1653608 | BC857BDW1T1G | 0,141 | 1 | BC857BDW1T1G | 0,210 | | BC857BDW1T1G | 0,199
54 | 1 TLC555 | SOIC-8 | IC28 | Arduino Shield | 1 | 9589880 | NE555DR | 0,300 | 1 | NE555D | 0,350 | | NE555D | 0,353
55 | 1 SN74LVC08APWR | TSSOP-14 | IC29 | Arduino Shield | 1 | 1102978 | SN74LVC08APWR | 0,236 | 1 | 296-1221-1-ND | 0,350 | 1 | | 0,335 | 1

771-
PMEG4005EH-T/R

STPS15H100CB-TR

| 530-0ZCJ0005FF2E

LTC3864EMSE#P
BF

LTC3864EMSE#
PBF
| 595-TPD4E002DRLR
| 595-TPD2E001DZDR
ADUM3160BRW Z-ND | 584-ADUM3160BRW Z
PCA21125T/Q900/ 1,1 | PCA21125T/Q90 0/1,1 | PCA21125T/Q90 0/1,1
| AT25256B-SSHL-B | AT25256B-SSHL-B

595-
SN74LVC08APW
R

Qty Part name

32 1 BAT54S
33 1 SKL16
1 SKL16

34 1 STPS15H100

35 1 50mA, polyfuse

36 3 60R@100MHz
3 60R@100MHz
1 60R@100MHz

37 1 LTC3864EMSE#PBF

38 1 DAC8552IDGKTG4

39 1 TS5A9411DCKT

40 1 ADS1120IPWR

41 1 LP339D
42 1 TPD4E002DRLR

43 1 TPD2E001DZDR

44 1 ADUM3160BRWZ

45 1 TLC5925IDBQR
46 2 Si8641EC-B-IS1
47 1 LP2951D
48 2 SI8651EC-B-IS1
49 1 LD1117S33TR

50 1 PCA21125T/Q900/1,1

51 1 AT25256B

52 1 W5500
53 1 BC857BS

54 1 TLC555
55 1 SN74LVC08APWR
Code Part Number MOQ € | Code / Part Number Unit price MOQ € | THT SMD | Best Order unit price Supplier Qty € | Line Cost € Unit price

9 BAS316

397-2914 BAS316,115 | 0,195 50 | BAS316,115 | 0,019 25 | 25 | TME | 0,019 € 25 | 0,463
670-8797 BAT54S | 0,202 10 | BAT54S.215 | 0,017 50 | 1 | TME | 0,017 € | 1 | 0,017
485-571 | PMEG4005EH | 0,101 20 | SKL16 | 0,095 | 5 | 2 | Farnell | 0,091 € 10 | 0,910
795-9075 | 0,924 | 5 | - | 2 | Mouser | 0,896 € | 2 | 1,792
- | SM005-60 | 0,092 10 | 1 | TME | 0,092 € | 1 | 0,092
669-4049 742792602 | 0,172 10 | LCBA-600 | 0,027 25 | 10 | TME | 0,027 € 10 | 0,269
0
- | | | - | | | 2 | Digikey | 3,960 € | 2 | 7,920
662-1498 DAC8552IDGKT | 6,524 | 1 | - | | | 2 | Farnell | 6,420 € | 2 | 12,840
459-459 | TS5A9411DCKT | 0,570 10 | - | 2 | Mouser | 0,534 € | 2 | 1,068
- | | | - | | | 2 | Mouser | 6,100 € | 2 | 12,200
661-2659 LP339DR | 0,175 10 | LP339D | 0,244 | 3 | 2 | RS | 0,175 € | 2 | 0,350
709-9060 TPD4E002DRLR | 0,199 10 | - | 1 | RS | 0,199 € | 1 | 0,199
812-0171 TPD2E001DZDR | 0,193 25 | - | 1 | RS | 0,193 € | 3 | 0,579
796-9041 | 5,880 | 1 | ADUM3160BRWZ-RL | 4,040 | 1 | 1 | TME | 4,040 € | 1 | 4,040
812-3984 TLC5925IDBQR | 1,109 10 | - | 1 | RS | 1,109 € | 1 | 1,109
753-2438 Out of stock | | | - | | | 2 | Mouser | 2,720 € | 2 | 5,440
796-8095 LP2951D | 0,613 | 5 | LP2951CM/NOPB | 0,495 | 1 | 2 | TME | 0,495 € | 2 | 0,990
753-2497 Si8651EC-B-IS1 | 3,038 | 1 | - | | | 2 | RS | 3,038 € | 2 | 6,076
714-0697 LD1117S33TR | 0,175 10 | LD1117S33TR | 0,183 | 3 | 1 | RS | 0,175 € | 1 | 0,175
- | | | - | | | 1 | Digikey | 1,610 € | 1 | 1,610
738-0079 | 1,267 | 2 | 25AA256-I/SN | 1,290 | 1 | 1 | Farnell | 1,190 € | 1 | 1,190
- | | | W5500 | 2,190 | 1 | 1 | TME | 2,190 € | 1 | 2,190
690-0101 | 0,022 25 | BC857BS | 0,027 25 | 1 | RS | 0,022 € | 1 | 0,022
662-4006 TLC555CDR | 0,218 10 | TLC555CDR | 0,384 | 3 | 1 | RS | 0,218 € | 1 | 0,218
662-8588 | 0,240 10 | - | 1 | Farnell | 0,236 € | 1 | 0,236

STPS15H100CB
-TR

ADUM3160BRW
Z

AT25256B-SSHL-B

BC857BDW1T1
G

SN74LVC08AP
WR

Qty Part name Package Reference designator Board name | Code Part Number MOQ € | Part Number Unit price MOQ € | Part Number Unit price MOQ Unit price €
| | | 595-TL783CKTTR
| | SN74LV1T34DB VR | SN74LV1T34DB VR
56 | 1 TL783CKTTR | TO-263-3 | IC3 | Power board | 2 | 2075436 | TL783CKTTR | 2,070 | 1 | 296-20778-1-ND | 2,270 | 1 | 2,220 | 1
57 | 1 SN74LV1T34DBVR | SOT-23 | IC30 | Arduino Shield | 1 | 2499914 | SN74LV1T34DBVR | 0,457 | 1 | 0,410 | 0,398
58 | 1 TPS3705-33D | SOIC-8 | IC31 | Arduino Shield | 1 | 2296066 | TPS3705-33D | 1,330 | 1 | TPS3705-33DR | 1,580 | TPS3705-33D | 1,840
59 | 1 SN74LVC2G02DCTR | SSOP-8 | IC32 | Arduino Shield | 1 | 1236358 | 0,452 | 1 | 0,590 | 0,570
60 | 1 LTC3260EMSE#PBF | MSOP-16 | IC4 | Power board | 2 | 2115838 | 7,660 | 1 | 6,780 | 1 | -
61 | 2 TL072CD | SOIC-8 | IC5, IC6 | Power board | 4 | 1467663 | TL072CDT | 0,252 | 5 | TL072CDT | 0,430 | TL072CDT | 0,416
62 | 1 LTC2050HVCS8#PBF | SOIC-8 | IC7 | Power board | 2 | 1330903 | 2,110 | 1 | 2,850 | 1 | -
63 | 1 MCP23S17-E/SS | SSOP-28 | IC8 | Power board | 2 | 1467675 | MCP23S17-E/SS | 1,280 | 1 | 1,270 | 1 | 1,320 | 1
64 | 1 REF5025AIDG4 | SOIC-8 | IC9 | Power board | 2 | 1439622 | REF5025AIDG4 | 3,720 | 1 | REF5025AIDR | 2,990 | REF5025AIDR | 2,910
65 | 1 1-726388-2 | THT | J2 | Arduino board | 1 | 2308760 | 1-726388-2 | 0,085 10 | A121493-ND | 0,210 | 1 | 571-1-726388-2 | 0,235 | 1
66 | 2 ZL303-03P | THT | JP9, JP10 | AUX PS | 2
67 | 2 RT424005 | THT | K_PAR, K_SER | Arduino Shield | 2
1 RT424005 | THT | K_DOUT2 | AUX PS | 1
3 | 9950168 | G2RL-2 5DC | 3,940 | 1 | RTE24005 | 2,920 | RTE24005 | 2,850
68 | 2 G6K-2F-5DC | SMD, relay | K_S1, K_S2 | Arduino Shield | 2 | 4446185 | G6K-2F 5DC | 5,870 | 1 | G6K-2F DC5 | 3,860 | G6K-2F-5DC | 4,000
69 | 1 SK 145/37,5 | KK1 | AUX PS | 1 | 4621414 | 3,530 | 1 | - | -
1 M3 nut | AUX PS | 1 | - | - | -
1 | AUX PS | 1 | 7096471 | 6797/3.0 | 1,870 100 | - | -
1 M3x8, black finish | AUX PS | 1 | - | - | -
70 | 1 RN112-4-02 | L1 | Power board | 2 | 2730089 | RN112-4-02 | 1,570 | 1 | 817-1535-ND | 2,510 | 1 | 631-RN112-4/02 | 2,290 | 1
71 | 1 470uH | SMD; 7.3mm x 7.3mm | L5 | AUX PS | 1 | 2455059 | SRR0745A-471M | 0,918 | 1 | SRR0745A-471M | 0,770 | SRR0745A-471M | 0,814
72 | 1 33uH - 7443551331 | SMD; 13.2mm x 12.8mm | L2 | Power board | 2 | 2211631 | 3,070 | 1 | 7443551331 | 3,380 | 7443551331 | 2,970
73 | 2 IHLP2020CZER3R3M11 SMD; 5.49mm x 5.18mm | L3, L4 | Power board | 4 | 1741325 | 1,410 | 5 | 2,160 | 1,030
74 | 1 TFT_320QVT | THT; 2x20-pin socket | LCD1 | Arduino Shield | 1 | 7992033 | M20-7832046 | 2,750 | 1 | M20-7832046 | 3,160 | M20-7832046 | 2,530
75 | 2 HSMG-C170 | 0805 Green | LED_O1, LED_O2 | Arduino Shield | 2 | 5790852 | HSMG-C170 | 0,204 10 | HSMG-C170 | 0,490 | 630-HSMG-C170 | 0,060
76 | 5 HSMH-C170 | 0805 Red | Arduino Shield | 5 | 5790840 | HSMH-C170 | 0,488 | 5 | HSMH-C170 | 0,440 | 630-HSMH-C170 | 0,060
77 | 1 HSMD-C170 | 0805 Orange | LED_PWR | Arduino Shield | 1 | 5790864 | HSMD-C170 | 0,240 | 5 | HSMD-C170 | 0,440 | 630-HSMD-C170 | 0,060
78 | 4 HSMY-C170 | 0805 Yellow | Arduino Shield | 4 | 5790876 | HSMY-C170 | 0,330 | 5 | HSMY-C170 | 0,440 | 630-HSMY-C170 | 0,060
79 | 1 10K/Beta:3570K | 0805 | NTC1 | Power board | 2 | 1612623 | 0,413 | 1 | 0,250 | 0,145
80 | 1 MOC3052 | SMD; SDIP-6 | OK1 | AUX PS | 1 | 2453236 | MOC3052SM | 0,884 | 1 | MOC3052SM | 0,910 | MOC3052SM | 0,750
SN74LVC2G02DC TR | SN74LVC2G02D CTR | SN74LVC2G02D CTR
| LTC3260EMSE#P BF | LTC3260EMSE# PBF-ND
LTC2050HVCS8#P BF | LTC2050HVCS8 #PBF-ND
| MCP23S17-E/SS-ND | 579-MCP23S17-E/SS

THT Heatsink for installation of Q21 and Q22 like on the picture here. (https://raw.githubusercontent.com/eez-open/psu-hw/master/Building%20instructions/AUX%20PS%20r5B9%20heatsink.JPG)

SK 145/37,5 STS-220

For mounting Q21, Q22 to
KK1
Washer externally
serrated M3, D=6mm

For mounting Q21, Q22 to
KK1
For mouniting Q21, Q22 to
KK1
THT, solder on the bottom
layer!

Würth -7443551331

IHLP2020CZER3R 3M11 | IHLP2020CZER3 R3M11 | IHLP2020CZER3 R3M11

LED_CC1, LED_CC2,
LED_PROG1, LED_PROG2,
LED_SP

LED_CV1, LED_CV2, LED_S1, LED_S2

| NTCS0805E3103J MT | NTCS0805E3103 JMT | NTCS0805E3103 JMT

Qty Part name

56 1 TL783CKTTR

57 1 SN74LV1T34DBVR

58 1 TPS3705-33D

59 1 SN74LVC2G02DCTR

60 1 LTC3260EMSE#PBF

61 2 TL072CD

62 1 LTC2050HVCS8#PBF

63 1 MCP23S17-E/SS

64 1 REF5025AIDG4
65 1 1-726388-2
66 2 ZL303-03P
67 2 RT424005
1 RT424005

68 2 G6K-2F-5DC
69 1 SK 145/37,5

1 M3 nut

1

1 M3x8, black finish

70 1 RN112-4-02

71 1 470uH

72 1 33uH - 7443551331

73 2 IHLP2020CZER3R3M11

74 1 TFT_320QVT
75 2 HSMG-C170

76 5 HSMH-C170

77 1 HSMD-C170
78 4 HSMY-C170

79 1 10K/Beta:3570K

80 1 MOC3052

Washer externally
serrated M3, D=6mm
Code Part Number MOQ € | Code / Part Number Unit price MOQ € | THT SMD | Best Order unit price Supplier Qty € | Line Cost € Unit price
| 660-7455 TL783CKTTR 1,904 5 | - | 2 | RS 1,904 € 2 | 3,808
- | | | - | | | 1 | Mouser | 0,398 € | 1 | 0,398
662-3331 TPS3705-33D | 0,528 | 5 | - | | | 1 | RS | 0,528 € | 1 | 0,528
- | | | SN74LVC2G02DCTR | 0,252 | 5 | 1 | TME | 0,252 € | 1 | 0,252
851-6768 | 5,800 | 1 | - | | | 2 | RS | 5,800 € | 2 | 11,600
857-907P TL072CD | 0,252 | 1 | TL072CD | 0,164 | 3 | 4 | TME | 0,164 € | 4 | 0,654
822-6746 | 2,155 | 2 | - | | 1 | 2 | Farnell | 2,110 € | 2 | 4,220
669-6452 | 1,168 | 5 | MCP23S17-E/SS | 1,290 | 1 | 2 | RS | 1,168 € | 2 | 2,336
404-304 | REF5025AID | 3,500 | 1 | - | 2 | Mouser | 2,910 € | 2 | 5,820
680-5772 1-726388-2 | 0,060 100 | 1-726388-2 | 0,082 10 | 1 | RS | 0,060 € | 1 | 0,060
ZL303-03P | 0,027 20 | 2 | TME | 0,027 € | 4 | 0,107
198-6898 RTE24005 | 4,676 | 1 | RT424005 | 1,260 | 1 | 3 | TME | 1,260 € | 3 | 3,780
683-9633 G6K2F5DC | 4,928 | 1 | G6K-2F-5DC | 2,490 | 1 | 2 | TME | 2,490 € | 2 | 4,980
- | | | - | | | 1 | Farnell | 3,530 € | 1 | 3,530
- | B3/BN117 | 0,005 100 | TME | 0,005 € | 1 | 0,005
- | B3/BN789 | 0,008 100 | TME | 0,008 € | 1 | 0,008
- | M3X8/D7985B | 0,019 100 | TME | 0,019 € | 1 | 0,019
219-3261 RN112-4-02 | 3,160 | 1 | - | | | 2 | Farnell | 1,570 € | 2 | 3,140
770-1182 DR74-471-R | 0,977 | 5 | DE0704-470 | 0,254 | 5 | 1 | TME | 0,254 € | 1 | 0,254
- | | | - | | | 2 | Mouser | 2,970 € | 2 | 5,940
748-6912 | 1,518 | 5 | - | | | 4 | Mouser | 1,030 € | 4 | 4,120
681-6851 M20-7832046 | 3,027 | 5 | ZL262-40DG | 0,329 | 2 | 1 | TME | 0,329 € | 2 | 0,658
435-6767 HSMG-C170 | 0,206 50 | HSMG-C170 | 0,095 | 5 | 2 | Mouser | 0,060 € | 2 | 0,120
486-0468 HSMH-C170 | 0,188 25 | HSMH-C170 | 0,057 10 | 5 | TME | 0,057 € | 5 | 0,287
486-0525 HSMD-C170 | 0,231 25 | HSMD-C170 | 0,059 10 | 1 | TME | 0,059 € | 1 | 0,059
486-0519 HSMY-C170 | 0,248 25 | HSMY-C170 | 0,060 10 | 4 | Mouser | 0,060 € | 4 | 0,240
697-4601 | 0,392 | 5 | NTCS0805E3103JMT | 0,190 | 5 | 2 | Mouser | 0,145 € | 2 | 0,290
761-3690 MOC3052SM | 0,739 | 5 | MOC3052SR2VM | 0,380 | 2 | 1 | TME | 0,380 € | 1 | 0,380

LTC3260EMSE#
PBF

LTC2050HVCS8
#PBF-ND

MCP23S17-
E/SS

IHLP2020CZER
3R3M01

NB12K00103JB
B

Qty | Part name | Package | Reference designator | Board name
Code | Part Number | MOQ | Part Number | MOQ | Part Number | MOQ Unit price
€

Unit price
€

Unit price
€
81 | 1 MOC3062 | SMD; SDIP-6 | OK2 | AUX PS | 1 | 2322554 | MOC3062SR2VM | 0,977 | 1 | MOC3062SM | 1,110 | MOC3062SM | 0,924
82 | 2 HCPL-181 | SOIC-4 | OK3, OK4 | AUX PS | 2
| 2 HCPL-181 | SOIC-4 | OK5, OK6 | Arduino Shield | 2
| | | | | 4 | 1244525 | HCPL-181-000E | 0,342 | 1 | HCPL-181-000E | 0,560 | HCPL-181-000E | 0,150
83 | 2 IRFR5305 | TO-252 | Q1, Q7 | Power board | 4 | 8649820 | IRFR5305PBF | 0,994 | 1 | | 0,810 | | 0,805
| Option #1: SPD30P06P | TO-252 | Q1, Q7 | Power board | 0 | 2480881 | SPD30P06P G | 0,980 | 1 | | 1,030 | | 1,020
84 | 5 MMBT5551 | SOT-23 | Q11, Q12, Q17, Q19, Q20 | Power board | 10 | 1459109 | MMBT5551LT1G | 0,167 | 5 | MMBT5551LT1G | 0,180 | MMBT5551LT1G | 0,163
85 | 4 MMBT5401 | SOT-23 | Q2, Q9, Q10, Q18 | Power board | 8 | 1459108 | MMBT5401LT1G | 0,167 10 | MMBT5401LT1G | 0,180 | MMBT5401LT1G | 0,163
86 | 2 BTA26-600 | THT | Q21, Q22 | AUX PS | 2 | 1057286 | BTA26-600BRG | 2,840 | 1 | BTA26-600BRG | 2,930 | BTA26-600BRG | 3,110
87 | 1 IRLL2705PBF | SOT-223 | Q13 | Power board | 2
| 1 IRLL2705PBF | SOT-223 | Q23 | AUX PS | 1
3 | 8651230 | IRLL2705PBF | 0,578 | 1 | 0,630 | 1 | 0,622 | 1
88 | 1 IRFR48ZPB | TO-252 | Q14 | Power board | 2 | 1013388 | IRFR48ZPBF | 1,310 | 1 | 1,090 | 1 | 1,110 | 1
89 | 5 IRLML2246TRPBF | SOT-23 | Q26, Q27, Q28, Q29, Q31 | Arduino Shield | 5

1 IRLML2246TRPBF SOT-23 Q15 Power board 2

| IRLML2246TRPB F | IRLML2246TRPB F
7 | 1888166 | IRLML2246TRPBF | 0,287 | 1 | 0,400 | 0,389
90 | 2 2N7002 | SOT-23 | Q24, Q25 | AUX PS | 2
| 3 2N7002 | SOT-23 | Q3, Q16, Q34 | Power board | 6
| 3 2N7002 | SOT-23 | Q30, Q32, Q33 | Arduino Shield | 3
| | | | | 11 | 1713823 | 2N7002-7-F | 0,135 | 5 | 2N7002LT1G | 0,130 | 2N7002LT1G | 0,118
91 | 1 IRFP250N | | Q4 | Power board | 2 | 8649260 | IRFP250NPBF | 2,080 | 1 | IRFP250NPBF | 1,870 | IRFP250NPBF | 1,870
92 | 1 BC857C | SOT-23 | Q5 | Power board | 2 | 8734771 | BC857C,215 | 0,022 10 | BC857CLT1G | 0,120 | BC857CLT1G | 0,109
93 | 2 BCP56-16.115 | SOT-223 | Q6, Q8 | Power board | 4 | 1081258 | BCP56-16,115 | 0,256 | 5 | BCP56-16T1G | 0,360 | BCP56-16,115 | 0,340
94 | 1 0R | 0805 | R56 | Power board | 2 | 9233750 | RC0805JR-070RL | 0,010 10 | RC2012J000CS | 0,014 | 0,012
95 | 6 100K 1% | 0805 | R12, R15, R22, R23, R73, R75 | Power board | 12
| 1 100K 1% | 0805 | R123 | AUX PS | 1
4 100K 1% 0805 R135, R146, R160, R178 Arduino Shield 4
| RCV0805100KFKE A | RC0805FR-07100KL | RC0805FR-07100KL
17 | 2352619 | 0,080 10 | 0,019 | 0,015
96 | 2 | 0805 | R43, R53 | Power board | 4 | 1577686 | ERA6AEB104V | 0,205 | 5 | 0,350 | CPF0805B100KE | 0,095
| | IRFR5305PBF-ND | 942-IRFR5305PBF
| | SPD30P06P GCT-ND | 726-SPD30P06PG
Option #2: SUD19P06-60 TO-252 Q1, Q7 Power board 0 | 2101465 SUD19P06-60-GE3 1,590 5 | SUD19P06-60-0,950 GE3 | SUD19P06-60-1,070 GE3

IRLL2705PBF-ND

942-
IRLL2705PBF

IRFR48ZTRLPBF
CT-ND

942-
IRFR48ZPBF

THT, solder on the bottom
layer! See pic here (https://github.com/eez-open/psu-hw/blob/master/Building%20instructions/Power%20board%20Q4%20pins%20bending.JPG) and here (https://github.com/eez-open/psu-hw/blob/master/Building%20instructions/Power%20board%20Q4%20mounting.JPG)

RC0805JR-070RL

100K 0.1% | RT0805BRD0710 0KL

Qty Part name

81 1 MOC3062
82 2 HCPL-181
2 HCPL-181

83 2 IRFR5305

Option #1: SPD30P06P

Option #2: SUD19P06-60

84 5 MMBT5551
85 4 MMBT5401

86 2 BTA26-600
87 1 IRLL2705PBF

1 IRLL2705PBF

88 1 IRFR48ZPB

89 5 IRLML2246TRPBF

1 IRLML2246TRPBF

90 2 2N7002

3 2N7002

3 2N7002

91 1 IRFP250N

92 1 BC857C
93 2 BCP56-16.115
94 1 0R

95 6 100K 1%
1 100K 1%
4 100K 1%

96 2 100K 0.1%

Code Part Number MOQ € | Code / Part Number Unit price MOQ € | THT SMD | Best Order unit price Supplier Qty € | Line Cost € Unit price
806-6064 MOC3062SM | 0,718 10 | MOC3062XSM | 0,410 | 1 | 1 | TME | 0,410 € | 1 | 0,410
693-5277 HCPL-181-000E | 0,343 10 | HCPL-181-000E | 0,250 | 2 | 4 | Mouser | 0,150 € | 4 | 0,600
543-2496 IRFR5305PBF | 0,994 | 1 | IRFR5305PBF | 0,540 | 1 | 4 | TME | 0,540 € | 2 | 1,080
898-6864 SPD30P06P G | 0,861 | 1 | SPD30P06PGBTMA1 | 0,780 | 1
545-0400 MMBT5551LT1G | 0,129 10 | MMBT5551 | 0,020 25 | 10 | TME | 0,020 € 25 | 0,510
545-0393 MMBT5401LT1G | 0,151 10 | MMBT5401 | 0,021 25 | 8 | TME | 0,021 € 25 | 0,513
714-0515 BTA26-600BRG | 3,038 | 1 | BTA26-600BRG | 2,540 | 1 | 2 | TME | 2,540 € | 2 | 5,080
540-9907 IRLL2705PBF | 0,260 | 1 | IRLL2705PBF | 0,307 | 1 | 3 | RS | 0,260 € | 3 | 0,780
688-7055 IRFR48ZPBF | 1,234 | 1 | IRFR48ZPBF | 0,540 | 1 | 2 | TME | 0,540 € | 2 | 1,080
760-4432 | 0,322 | 5 | IRLML2246TRPBF | 0,100 | 5 | 7 | TME | 0,100 € | 7 | 0,700
545-0012 2N7002LT1G | 0,108 50 | 2N7002LT1G | 0,019 25 | 11 | TME | 0,019 € 25 | 0,475
541-0042 IRFP250NPBF | 2,100 | 1 | IRFP250NPBF | 1,060 | 1 | 2 | TME | 1,060 € | 2 | 2,120
690-0105 BC857CLT1G | 0,102 25 | BC857C-DIO | 0,020 25 | 2 | TME | 0,020 € | 2 | 0,040
773-7633 BCP56-16T3G | 0,242 10 | BCP56-16.115 | 0,106 | 5 | 4 | TME | 0,106 € | 4 | 0,424
679-0800 | 0,020 50 | SMD0805-0R | 0,006 100 | 2 | TME | 0,006 € 15 | 0,090
223-0691 CRG0805F100K | 0,007 50 | SMD0805-100K-1% | 0,008 100 | 17 | RS | 0,007 € 17 | 0,119
666-2673 | 0,112 | 5 | RN73C2A100KBTDF | 0,513 | 2 | 4 | Mouser | 0,095 € | 4 | 0,380

IRLML2246TRP
BF

CRCW08050000
Z0EA

CPF0805B100K
E

Qty | Part name | Package | Reference designator | Board name
Code | Part Number | MOQ | Part Number | MOQ | Part Number | MOQ Unit price
€

Unit price
€
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

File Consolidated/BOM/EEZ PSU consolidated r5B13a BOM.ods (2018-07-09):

 |  |  |  |  |  |  | Farnell / Element14 |  |  |  | Digi-Key |  |  | Mouser |  |  | RS Components |  |  |  | TME |  |  |  |  | Price calculation for 1 set
# | Qty | Part name | Package | Reference designator | Board name | Qty | Code | Part Number | Unit price € | MOQ | Part Number | Unit price € | MOQ | Part Number | Unit price € | MOQ | Code | Part Number | Unit price € | MOQ | Code / Part Number | Unit price € | MOQ | THT | SMD | Best Supplier | Lowest unit price € | Order Qty | Line Cost €
1 | 1 | 2x3-pin socket | THT; 2x3-pin socket | MCU-ICSP | Arduino Shield | 1 | 7991983 | M20-7830346 | 1,210 | 10 | M20-7830346 | 1,000 |  | M20-7830346 | 0,940 |  | 681-6832 | M20-7830346 | 0,899 | 5 | ZL262-6DG | 0,070 | 10 | 1 |  | TME | 0,070 € | 1 | 0,070
2 | 17 | 100n 16V X7R | 0603 | C9, C20, C32, C43, C44, C45, C49, C50, C51, C54, C56, C59, C63, C65, C69, C72, C73 | Power board | 34
 | 5 | 100n 16V X7R | 0603 | C81, C82, C83, C84, C85 | AUX PS | 5
 | 27 | 100n 16V X7R | 0603 | C97, C98, C99, C100, C101, C102, C104, C106, C107, C108, C109, C111, C113, C114, C121, C122, C123, C124, C125, C126, C127, C128, C132, C134, C136, C139, C141 | Arduino Shield | 27
 |  |  |  |  |  | 66 | 2496832 | 0603B104K160CT | 0,012 | 10 | 0603YC104KAT2A | 0,010 |  | 06033C104K4T4A | 0,025 |  | 391-246 | 0603YC104JAT2A | 0,004 | 50 | CL10B104KO8NNNC | 0,004 | 100 |  | 66 | RS | 0,004 € | 100 | 0,400
3 | 1 | 220u 16V | SMD ELCO; Ø6.3 x 7.7mm | C78 | AUX PS | 1 | 1870605 | MCESL16V227M6.3X7.7 | 0,213 | 10 | 399-6679-1-ND | 0,410 | 1 | 80-EDK227M016A9HAA | 0,407 | 1 | 839-1770 | 865080345012 | 0,280 | 10 | SC1C227M6L07KVR | 0,061 | 10 |  | 1 | TME | 0,061 € | 1 | 0,061
4 | 5 | 10n 50V X7R | 0805 | C118, C131, C135, C137, C138 | Arduino Shield | 5
 | 8 | 10n 50V X7R | 0805 | C25, C28, C35, C42, C47, C62, C70, C74 | Power board | 16
 |  |  |  |  |  | 21 | 1759246 | MC0805B103K500CT | 0,009 | 10 | CL21B103KBCNNNC | 0,027 |  | GRM216R71H103KA01D | 0,014 |  | 461-4013 | CC0805KRX7R9BB103 | 0,007 | 50 | CL21B103JBANNNC | 0,006 | 100 |  | 21 | TME | 0,006 € | 20 | 0,120
5 | 2 | 10u 50V X7R | 1210 | C90, C110 | Arduino Shield | 2
 | 7 | 10u 50V X7R | 1210 | C10, C16, C22, C24, C29, C30, C55 | Power board | 14
 |  |  |  |  |  | 16 | 2362133 | GRM32ER71H106KA12L | 0,748 | 1 | CL32B106KBJNNWE | 0,335 |  | GRM32ER71H106KA12L | 0,376 |  | 766-1214 | CL32B106KBJNNNE | 0,601 | 10 | CL32B106KBJNNNE | 0,201 | 10 |  | 16 | TME | 0,201 € | 16 | 3,216
6 | 2 | 10u 10V | 1206, Tantalum | C105, C129 | Arduino Shield | 2
 | 2 | 10u 10V | 1206, Tantalum | C23, C31 | Power board | 4
 |  |  |  |  |  | 6 | 1457413 | T491A106K010AT | 0,260 | 5 | T491A106K010AT | 0,340 |  | T491A106K010AT | 0,344 |  | 538-2278 | T491A106K010AT | 0,196 | 10 | T491A106K010AT | 0,085 | 10 |  | 6 | TME | 0,085 € | 10 | 0,845
7 | 2 | 120p 50V NP0 | 0805 / 0603 | C17, C39 | Power board | 4 | 1414667 | C0805C121J5GACTU | 0,044 | 10 | CL21C121JBANNNC | 0,058 |  | C0805C121J5GACTU | 0,031 |  | 723-6209 | GRM2165C1H121JA01D | 0,035 | 100 | CL21C121JBANNNP | 0,007 | 100 |  | 4 | TME | 0,007 € | 10 | 0,069
8 | 2 | 18p 50V NP0 | 0805 / 0603 | C116, C120 | Arduino Shield | 2 | 2320820 | MC0805N180J101CT | 0,026 | 10 | CL21C180JBANNNC | 0,090 |  | C0805C180J5GACTU | 0,100 |  | 648-0935 | C0805C180J5GACTU | 0,157 | 10 | CL21C180JBANNNC | 0,071 | 100 |  | 2 | Farnell | 0,026 € | 2 | 0,053
9 | 2 | 1n 50V NP0 | 0805 / 0603 | C52, C53 | Power board | 4 | 1759227 | MC0805N102J500CT | 0,029 | 10 | CL21C102JBCNNNC | 0,065 |  | C0805C102J5GACTU | 0,038 |  | 378-710 | 0805CG102J9BB | 0,021 | 25 | CL21C102JBCNNNC | 0,010 | 100 |  | 4 | TME | 0,010 € | 10 | 0,097
10 | 2 | 1u 100V X7R | 1206, 100V | C8, C33 | Power board | 4 | 2320876 | MC1206B105K101CT | 0,200 | 5 | CL31B105KCHNNNE | 0,253 |  | GRM31CR72A105KA01L | 0,227 |  | 740-7590 | C3216X7R2A105K160AA | 0,174 | 10 | GRM31CR72A105KA01L | 0,128 | 10 |  | 4 | TME | 0,128 € | 10 | 1,279
11 | 7 | 1u 50V X7R | 0805, 50V | C11, C26, C46, C48, C58, C64, C66 | Power board | 14
 | 1 | 1u 50V X7R | 0805, 50V | C156 | Arduino board | 1
 |  |  |  |  |  | 15 | 2118131 | C0805C105K5RACTU | 0,215 | 5 | CL21B105KBFNNNE | 0,129 |  | 08055C105K4T2A | 0,135 |  | 766-1062 | CL21B105KBFNNNF | 0,041 | 100 | CL21B105KBFNNNG | 0,014 | 100 |  | 15 | TME | 0,014 € | 15 | 0,214
12 | 1 | 22n 50V X7R | 0805 | C115 | Arduino Shield | 1 | 1759252 | MC0805B223K500CT | 0,016 | 10 | CL21B223KBANNNC | 0,058 |  | C0805C223K5RAC | 0,031 |  | 464-6701 | 08055C223KAT2A | 0,015 | 50 | CL21B223KBANNNC | 0,008 | 100 |  | 1 | TME | 0,008 € | 10 | 0,084
13 | 5 | 2n2 50V NP0 | 0805 / 0603 | C36, C37, C38, C40, C71 | Power board | 10 | 1759236 | MC0805N222J500CT | 0,052 | 10 | CL21C222JBFNNNG | 0,078 |  | GRM2165C1H222JA01D | 0,076 |  | 802-9905 | C0805C222J5GACTU | 0,043 | 100 | GRM2165C1H222JA01D | 0,015 | 100 |  | 10 | TME | 0,015 € | 10 | 0,145
14 | 2 | 22u 50V | SMD ELCO; Ø8x10.2mm | C89, C94 | Arduino board | 2 | 2326151 | EEE1HA220WAP | 0,341 | 1 | 493-9884-1-ND | 0,280 | 1 | 647-UWT1H220MCL6GS | 0,339 | 1 | 520-2009 | UWT1H220MCL1GB | 0,174 | 25 | UWT1H220MCL6GS | 0,009 | 10 |  | 2 | TME | 0,009 € | 5 | 0,047
15 | 4 | 3n3 50V X7R or NP0 | 0805 / 0603 | C60, C61, C67, C68 | Power board | 8 | 1759291 | MC0805B332K101CT | 0,015 | 10 | CL21B332KBANNNC | 0,045 |  | C0805C332K5RAC | 0,024 |  | 237-7009 | GRM216R71H332KA01D | 0,038 | 50 | CL21B332KBANNNC | 0,007 | 100 |  | 8 | TME | 0,007 € | 10 | 0,069
16 | 1 | 470n 50V X7R | 0805, 50V | C7 | Power board | 2
 | 2 | 470n 50V X7R | 0805, 50V | C87, C92 | Arduino Shield | 2
 |  |  |  |  |  | 4 | 2470492 | GRM21BR71H474KA88L | 0,163 | 5 | CL21B474KBFNFNE | 0,139 |  | C0805C474K5RACTU | 0,103 |  | 766-1053 | CL21B474KBF4PNG | 0,085 | 50 | CL21B474KBFNNNG | 0,015 | 100 |  | 4 | TME | 0,015 € | 10 | 0,153
17 | 2 | 470p 50V NP0 | 0805 / 0603 | C14, C19 | Power board | 4 | 1759217 | MC0805N471J500CT | 0,023 | 10 | CL21C471JBANNNC | 0,090 |  | 08055A471JAT2A | 0,091 |  | 378-700 | 0805CG471J9BB | 0,021 | 25 | CL21C471JBANNNC | 0,009 | 100 |  | 4 | TME | 0,009 € | 2 | 0,018
18 | 2 | 47n 50V X7R | 0805 | C133, C140 | Arduino Shield | 2
 | 1 | 47n 50V X7R | 0805 | C79 | AUX PS | 1
 |  |  |  |  |  | 3 | 2496983 | 0805B473K500CT | 0,023 | 10 | CL21B473KBCNNNC | 0,090 |  | 08055C473KAT2A | 0,091 |  | 391-303 | 08055C473KAT2A | 0,011 | 50 | CC0805KRX7R9473 | 0,008 | 100 |  | 3 | TME | 0,008 € | 3 | 0,025
19 | 1 | 47n 400V Polyester Film | THT R=7,5mm | C76 | AUX PS | 1 | 2468839 | B32520E6473K000 | 0,358 | 1 | - |  |  | - |  |  | 668-9993 | B32520C6473K189 | 0,241 | 10 | - |  |  | 1 |  | RS | 0,241 € | 1 | 0,241
20 | 2 | 47p 50V NP0 | 0805 / 0603 | C34, C41 | Power board | 4 | 1414692 | C0805C470J5GACTU | 0,028 | 10 | CL21C470JBANNNC | 0,043 |  | C0805C470J5GACTU | 0,029 |  | 264-4270 | C0805C470J5GACTU | 0,014 | 25 | CC0805JRNPO9470 | 0,007 | 100 |  | 4 | TME | 0,007 € | 10 | 0,074
21 | 1 | 47u 35V | SMD ELCO, Ø6.3 x 5.8mm | C103 | Arduino Shield | 1 | 9695850 | EEEFK1V470P | 0,493 | 1 | EEEFK1V470P | 0,440 |  | EEEFK1V470P | 0,443 |  | 565-623 | EEEFK1V470AP | 0,165 | 5 | EEEFK1V470P | 0,157 | 5 |  | 1 | TME | 0,157 € | 10 | 1,572
22 | 1 | 47u 50V | SMD ELCO; Ø8x10.2mm | C13 | Power board | 2 | 9695931 | EEEFK1H470P | 0,622 | 1 | PCE3815CT-ND | 0,600 | 1 | 667-EEE-FK1H470P | 0,754 | 1 | 537-0590 | EEEFK1H470P | 0,170 | 5 | EEEFK1H470P | 0,197 | 5 |  | 2 | RS | 0,170 € | 5 | 0,850
23 | 4 | 4n7 100V X7R | 0805 | C1, C2, C4, C18 | Power board | 8
 | 4 | 4n7 100V X7R | 0805 | C88, C91, C93, C95 | Arduino board | 4
 |  |  |  |  |  | 12 | 1759293 | MC0805B472K101CT | 0,019 | 10 | CL21B472KCANNNC | 0,065 |  | GRM21AR72D472KW01D | 0,050 |  | 698-3364 | 08051C472KAZ2A | 0,036 | 25 | CL21B472KCANNNC | 0,006 | 100 |  | 12 | TME | 0,006 € | 20 | 0,126
24 | 1 | 4u7 10V | 1206, Tantalum | C130 | Arduino Shield | 1
 | 2 | 4u7 10V | 1206, Tantalum | C21, C57 | Power board | 4
 |  |  |  |  |  | 5 | 1457428 | T491A475K016AT | 0,238 | 5 | T491A475K010AT | 0,310 |  | T491A475K010AT | 0,299 |  | 538-2341 | T491A475K016AT | 0,179 | 10 | T491A475M010AT | 0,128 | 5 |  | 5 | TME | 0,128 € | 5 | 0,640
25 | 2 | 4u7 100V X7R | 1210, 100V, X7R | C5, C6 | Power board | 4 | 2211140 | CGA6M3X7S2A475K200AB | 1,560 | 1 | GRJ32DC72A475KE11L | 1,240 |  | GRJ32DC72A475KE11L | 1,250 |  | 915-5415 | CGA6M3X7S2A475K200AB | 0,686 | 5 | - |  |  |  | 4 | RS | 0,686 € | 4 | 2,744
26 | 2 | 6n8 50V X7R or NP0 | 0603 | C117, C119 | Arduino Shield | 2 | 1759100 | MC0603B682K500CT | 0,007 | 10 | CL10B682KB8NNNC | 0,090 |  | GRM188R71H682KA01J | 0,091 |  | 147-825 | C0603C682K5RACTU | 0,007 | 50 | CL10B682JB8NNNC | 0,004 | 100 |  | 2 | TME | 0,004 € | 10 | 0,042
27 | 1 | 6n8 (X1 / Y2) PP Film 300Vac 1000Vdc | THT R=10mm | C75 | AUX PS | 1 | 2478385 | R413F16804000M | 0,528 | 1 | R413F16804000M | 0,520 |  | R413F16804000M | 0,525 |  | 871-2489 | 890334023003CS | 0,420 | 10 | MKP-Y2-6N8 | 0,158 | 5 | 1 |  | TME | 0,158 € | 1 | 0,158
28 | 1 | 1F 5,5V Backup Cap | THT | C112 | Arduino Shield | 1 | 9697497 | EEC-S5R5H105 | 4,660 | 1 | EEC-S5R5H105 | 3,480 |  | EEC-S5R5H105 | 3,510 |  | 339-6843 | EECS5R5H105 | 3,556 | 1 | EECS5R5H105 | 2,190 | 1 | 1 |  | TME | 2,190 € | 1 | 2,190
29 | 1 | 100u 63V | SMD ELCO; Ø10 x 10.2mm | C15 | Power board | 2 | 9696040 | EEEFK1J101P | 0,846 | 1 | EEE-FK1J101P | 0,930 |  | EEE-FK1J101P | 0,932 |  | 708-3623 | EEEFK1J101P | 0,641 | 5 | EEEFK1J101P | 0,380 | 5 |  | 2 | TME | 0,380 € | 2 | 0,760
30 | 2 | 18u 50V | SMD ELCO Polymer; Ø8x6.9mm | C3 | Power bord | 2
 | 2 | 18u 50V | SMD ELCO Polymer; Ø8x6.9mm | C86, C96 | Arduino Shield | 2
 |  |  |  |  |  | 4 | 2354813 | 50SVPF18M | 1,830 | 1 | P18942CT-ND | 1,430 | 1 | 667-50SVPF18M | 1,720 | 1 | - |  |  |  | - |  |  |  | 4 | Digikey | 1,430 € | 5 | 7,150
31 | 1 | BAS316 | SOD-323 | D12 | AUX PS | 1
 | 6 | BAS316 | SOD-323 | D13, D14, D15, D16, D18, D21 | Arduino Shield | 6
 | 9 | BAS316 | SOD-323 | D2, D3, D4, D5, D6, D7, D8, D9, D10 | Power board | 18
 |  |  |  |  |  | 25 | 8734275 | BAS316,115 | 0,192 | 5 | BAS316,115 | 0,175 |  | BAS316,115 | 0,174 |  | 397-2914 | BAS316,115 | 0,195 | 50 | BAS316,115 | 0,019 | 25 |  | 25 | TME | 0,019 € | 25 | 0,463
32 | 1 | BAT54S | SOT-23 | D19 | Arduino Shield | 1 | 1621835 | BAT54S | 0,125 | 10 | BAT54SLT1G | 0,150 |  | BAT54SLT1G | 0,145 |  | 670-8797 | BAT54S | 0,202 | 10 | BAT54S.215 | 0,017 | 50 |  | 1 | TME | 0,017 € | 1 | 0,017
33 | 1 | SKL16 | SOD-123F | D11 | AUX PS | 1
 | 1 | SKL16 | SOD-123F | D20 | Arduino Shield | 1
 |  |  |  |  |  | 2 | 1510688 | PMEG4005EH | 0,091 | 5 | 1727-3876-1-ND | 0,430 | 1 | 771-PMEG4005EH-T/R | 0,405 | 1 | 485-571 | PMEG4005EH | 0,101 | 20 | SKL16 | 0,095 | 5 |  | 2 | Farnell | 0,091 € | 10 | 0,910
34 | 1 | STPS15H100 | TO-252 | D1 | Power board | 2 | 2344052 | STPS15H100CB-TR | 1,070 | 1 | STPS15H100CB | 0,900 |  | STPS15H100CB | 0,896 |  | 795-9075 | STPS15H100CB-TR | 0,924 | 5 | - |  |  |  | 2 | Mouser | 0,896 € | 2 | 1,792
35 | 1 | 50mA, polyfuse | 1210 | F1 | Arduino board | 1 | 1861176 | MC36203 | 0,163 | 5 | 507-1476-1-ND | 0,200 | 1 | 530-0ZCJ0005FF2E | 0,101 | 1 | - |  |  |  | SM005-60 | 0,092 | 10 |  | 1 | TME | 0,092 € | 1 | 0,092
36 | 3 | 60R@100MHz | 0603 Ferrite Bead | FB1, FB2, FB3 | Power board | 6
 | 3 | 60R@100MHz | 0603 Ferrite Bead | FB4, FB5, FB6 | AUX PS | 3
 | 1 | 60R@100MHz | 0603 Ferrite Bead | FB7 | Arduino Shield | 1
 |  |  |  |  |  | 10 | 1635704 | 742792602 | 0,210 | 1 | 742792602 | 0,210 |  | 742792602 | 0,160 |  | 669-4049 | 742792602 | 0,172 | 10 | LCBA-600 | 0,027 | 25 |  | 10 | TME | 0,027 € | 10 | 0,269
 |  |  |  |  |  |  |  |  |  |  |  |  |  |  |  |  |  |  |  |  |  |  |  |  | 0
37 | 1 | LTC3864EMSE#PBF | MSOP-12 | IC1 | Power board | 2 | 2293128 | LTC3864EMSE#PBF | 4,520 | 1 | LTC3864EMSE#PBF | 3,960 |  | - |  |  | - |  |  |  | - |  |  |  | 2 | Digikey | 3,960 € | 2 | 7,920
38 | 1 | DAC8552IDGKTG4 | MSOP-8 (VSSOP-8) | IC10 | Power board | 2 | 1329584 | DAC8552IDGKTG4 | 6,420 | 1 | DAC8552IDGKT | 7,660 |  | DAC8552IDGKR | 6,510 |  | 662-1498 | DAC8552IDGKT | 6,524 | 1 | - |  |  |  | 2 | Farnell | 6,420 € | 2 | 12,840
39 | 1 | TS5A9411DCKT | SC-70 | IC12 | Power board | 2 | 1755582 | TS5A9411DCKT | 1,050 | 1 | TS5A9411DCKR | 0,560 |  | TS5A9411DCKR | 0,534 |  | 459-459 | TS5A9411DCKT | 0,570 | 10 | - |  |  |  | 2 | Mouser | 0,534 € | 2 | 1,068
40 | 1 | ADS1120IPWR | TSSOP-16 | IC13 | Power board | 2 | 2402249 | ADS1120IPWR | 6,760 | 1 | ADS1120IPWR | 6,250 |  | ADS1120IPWR | 6,100 |  | - |  |  |  | - |  |  |  | 2 | Mouser | 6,100 € | 2 | 12,200
41 | 1 | LP339D | SOIC-14 | IC14 | Power board | 2 | 9589686 | LP339D | 0,573 | 1 | LP339DR | 0,520 |  | LP339DR | 0,498 |  | 661-2659 | LP339DR | 0,175 | 10 | LP339D | 0,244 | 3 |  | 2 | RS | 0,175 € | 2 | 0,350
42 | 1 | TPD4E002DRLR |  | IC15 | AUX PS | 1 | 1755329 | TPD4E002DRLR | 0,275 | 1 | 296-21694-1-ND | 0,660 | 1 | 595-TPD4E002DRLR | 0,594 | 1 | 709-9060 | TPD4E002DRLR | 0,199 | 10 | - |  |  |  | 1 | RS | 0,199 € | 1 | 0,199
43 | 1 | TPD2E001DZDR |  | IC16 | AUX PS | 1 | 2335446 | TPD2E001DZDR | 0,506 | 1 | 296-24770-1-ND | 0,580 | 1 | 595-TPD2E001DZDR | 0,519 | 1 | 812-0171 | TPD2E001DZDR | 0,193 | 25 | - |  |  |  | 1 | RS | 0,193 € | 3 | 0,579
44 | 1 | ADUM3160BRWZ |  | IC17 | AUX PS | 1 | 1843660 | ADUM3160BRWZ | 7,070 | 1 | ADUM3160BRWZ-ND | 7,290 | 1 | 584-ADUM3160BRWZ | 6,660 | 1 | 796-9041 | ADUM3160BRWZ | 5,880 | 1 | ADUM3160BRWZ-RL | 4,040 | 1 |  | 1 | TME | 4,040 € | 1 | 4,040
45 | 1 | TLC5925IDBQR | SSOP-24 | IC18 | Arduino Shield | 1 | 1694438 | TLC5925IDBQR | 1,520 | 1 | TLC5925IDBQR | 1,370 |  | TLC5925IDBQR | 1,330 |  | 812-3984 | TLC5925IDBQR | 1,109 | 10 | - |  |  |  | 1 | RS | 1,109 € | 1 | 1,109
46 | 2 | Si8641EC-B-IS1 | SOIC-16 | IC19, IC23 | Arduino Shield | 2 | 2423294 | Si8641EC-B-IS1 | 3,210 | 1 | Si8641EC-B-IS1 | 2,780 |  | Si8641EC-B-IS1 | 2,720 |  | 753-2438 | Out of stock |  |  | - |  |  |  | 2 | Mouser | 2,720 € | 2 | 5,440
47 | 1 | LP2951D | SOIC-8 | IC2 | Power board | 2 | 1755066 | LP2951D | 0,573 | 1 | LP2951DR | 0,520 |  | LP2951DR | 0,498 |  | 796-8095 | LP2951D | 0,613 | 5 | LP2951CM/NOPB | 0,495 | 1 |  | 2 | TME | 0,495 € | 2 | 0,990
48 | 2 | SI8651EC-B-IS1 | SOIC-16 | IC20, IC21 | Arduino Shield | 2 | 2423323 | SI8651EC-B-IS1 | 3,150 | 1 | SI8651EC-B-IS1 | 3,190 |  | SI8651EC-B-IS1 | 3,060 |  | 753-2497 | Si8651EC-B-IS1 | 3,038 | 1 | - |  |  |  | 2 | RS | 3,038 € | 2 | 6,076
49 | 1 | LD1117S33TR | TO-252 | IC22 | Arduino Shield | 1 | 1202826 | LD1117S33TR | 0,187 | 5 | 497-1242-1-ND | 0,400 | 1 | 511-LD1117S33 | 0,403 | 1 | 714-0697 | LD1117S33TR | 0,175 | 10 | LD1117S33TR | 0,183 | 3 |  | 1 | RS | 0,175 € | 1 | 0,175
50 | 1 | PCA21125T/Q900/1,1 | TSSOP-14 | IC24 | Arduino Shield | 1 | 2400445 | PCA21125T/Q900/1,1 | 1,870 | 1 | PCA21125T/Q900/1,1 | 1,610 |  | PCA21125T/Q900/1,1 | 1,660 |  | - |  |  |  | - |  |  |  | 1 | Digikey | 1,610 € | 1 | 1,610
51 | 1 | AT25256B | SOIC-8 | IC25 | Arduino Shield | 1 | 1841577 | AT25256B-SSHL-B | 1,190 | 1 | AT25256B-SSHL-B | 1,300 |  | AT25256B-SSHL-B | 1,290 |  | 738-0079 | AT25256B-SSHL-B | 1,267 | 2 | 25AA256-I/SN | 1,290 | 1 |  | 1 | Farnell | 1,190 € | 1 | 1,190
52 | 1 | W5500 | LQFP-48 | IC26 | Arduino Shield | 1 | - |  |  |  | W5500 | 3,750 |  | W5500 | 2,390 |  | - |  |  |  | W5500 | 2,190 | 1 |  | 1 | TME | 2,190 € | 1 | 2,190
53 | 1 | BC857BS | SOT-363 | IC27 | Arduino Shield | 1 | 1653608 | BC857BDW1T1G | 0,141 | 1 | BC857BDW1T1G | 0,210 |  | BC857BDW1T1G | 0,199 |  | 690-0101 | BC857BDW1T1G | 0,022 | 25 | BC857BS | 0,027 | 25 |  | 1 | RS | 0,022 € | 1 | 0,022
54 | 1 | TLC555 | SOIC-8 | IC28 | Arduino Shield | 1 | 9589880 | NE555DR | 0,300 | 1 | NE555D | 0,350 |  | NE555D | 0,353 |  | 662-4006 | TLC555CDR | 0,218 | 10 | TLC555CDR | 0,384 | 3 |  | 1 | RS | 0,218 € | 1 | 0,218
55 | 1 | SN74LVC08APWR | TSSOP-14 | IC29 | Arduino Shield | 1 | 1102978 | SN74LVC08APWR | 0,236 | 1 | 296-1221-1-ND | 0,350 | 1 | 595-SN74LVC08APWR | 0,335 | 1 | 662-8588 | SN74LVC08APWR | 0,240 | 10 | - |  |  |  | 1 | Farnell | 0,236 € | 1 | 0,236
56 | 1 | TL783CKTTR | TO-263-3 | IC3 | Power board | 2 | 2075436 | TL783CKTTR | 2,070 | 1 | 296-20778-1-ND | 2,270 | 1 | 595-TL783CKTTR | 2,220 | 1 | 660-7455 | TL783CKTTR | 1,904 | 5 | - |  |  |  | 2 | RS | 1,904 € | 2 | 3,808
57 | 1 | SN74LV1T34DBVR | SOT-23 | IC30 | Arduino Shield | 1 | 2499914 | SN74LV1T34DBVR | 0,457 | 1 | SN74LV1T34DBVR | 0,410 |  | SN74LV1T34DBVR | 0,398 |  | - |  |  |  | - |  |  |  | 1 | Mouser | 0,398 € | 1 | 0,398
58 | 1 | TPS3705-33D | SOIC-8 | IC31 | Arduino Shield | 1 | 2296066 | TPS3705-33D | 1,330 | 1 | TPS3705-33DR | 1,580 |  | TPS3705-33D | 1,840 |  | 662-3331 | TPS3705-33D | 0,528 | 5 | - |  |  |  | 1 | RS | 0,528 € | 1 | 0,528
59 | 1 | SN74LVC2G02DCTR | SSOP-8 | IC32 | Arduino Shield | 1 | 1236358 | SN74LVC2G02DCTR | 0,452 | 1 | SN74LVC2G02DCTR | 0,590 |  | SN74LVC2G02DCTR | 0,570 |  | - |  |  |  | SN74LVC2G02DCTR | 0,252 | 5 |  | 1 | TME | 0,252 € | 1 | 0,252
60 | 1 | LTC3260EMSE#PBF | MSOP-16 | IC4 | Power board | 2 | 2115838 | LTC3260EMSE#PBF | 7,660 | 1 | LTC3260EMSE#PBF-ND | 6,780 | 1 | - |  |  | 851-6768 | LTC3260EMSE#PBF | 5,800 | 1 | - |  |  |  | 2 | RS | 5,800 € | 2 | 11,600
61 | 2 | TL072CD | SOIC-8 | IC5, IC6 | Power board | 4 | 1467663 | TL072CDT | 0,252 | 5 | TL072CDT | 0,430 |  | TL072CDT | 0,416 |  | 857-907P | TL072CD | 0,252 | 1 | TL072CD | 0,164 | 3 |  | 4 | TME | 0,164 € | 4 | 0,654
62 | 1 | LTC2050HVCS8#PBF | SOIC-8 | IC7 | Power board | 2 | 1330903 | LTC2050HVCS8#PBF | 2,110 | 1 | LTC2050HVCS8#PBF-ND | 2,850 | 1 | - |  |  | 822-6746 | LTC2050HVCS8#PBF-ND | 2,155 | 2 | - |  | 1 |  | 2 | Farnell | 2,110 € | 2 | 4,220
63 | 1 | MCP23S17-E/SS | SSOP-28 | IC8 | Power board | 2 | 1467675 | MCP23S17-E/SS | 1,280 | 1 | MCP23S17-E/SS-ND | 1,270 | 1 | 579-MCP23S17-E/SS | 1,320 | 1 | 669-6452 | MCP23S17-E/SS | 1,168 | 5 | MCP23S17-E/SS | 1,290 | 1 |  | 2 | RS | 1,168 € | 2 | 2,336
64 | 1 | REF5025AIDG4 | SOIC-8 | IC9 | Power board | 2 | 1439622 | REF5025AIDG4 | 3,720 | 1 | REF5025AIDR | 2,990 |  | REF5025AIDR | 2,910 |  | 404-304 | REF5025AID | 3,500 | 1 | - |  |  |  | 2 | Mouser | 2,910 € | 2 | 5,820
65 | 1 | 1-726388-2 | THT | J2 | Arduino board | 1 | 2308760 | 1-726388-2 | 0,085 | 10 | A121493-ND | 0,210 | 1 | 571-1-726388-2 | 0,235 | 1 | 680-5772 | 1-726388-2 | 0,060 | 100 | 1-726388-2 | 0,082 | 10 | 1 |  | RS | 0,060 € | 1 | 0,060
66 | 2 | ZL303-03P | THT | JP9, JP10 | AUX PS | 2 |  |  |  |  |  |  |  |  |  |  |  |  |  |  | ZL303-03P | 0,027 | 20 | 2 |  | TME | 0,027 € | 4 | 0,107
67 | 2 | RT424005 | THT | K_PAR, K_SER | Arduino Shield | 2
 | 1 | RT424005 | THT | K_DOUT2 | AUX PS | 1
 |  |  |  |  |  | 3 | 9950168 | G2RL-2 5DC | 3,940 | 1 | RTE24005 | 2,920 |  | RTE24005 | 2,850 |  | 198-6898 | RTE24005 | 4,676 | 1 | RT424005 | 1,260 | 1 | 3 |  | TME | 1,260 € | 3 | 3,780
68 | 2 | G6K-2F-5DC | SMD, relay | K_S1, K_S2 | Arduino Shield | 2 | 4446185 | G6K-2F 5DC | 5,870 | 1 | G6K-2F DC5 | 3,860 |  | G6K-2F-5DC | 4,000 |  | 683-9633 | G6K2F5DC | 4,928 | 1 | G6K-2F-5DC | 2,490 | 1 |  | 2 | TME | 2,490 € | 2 | 4,980
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

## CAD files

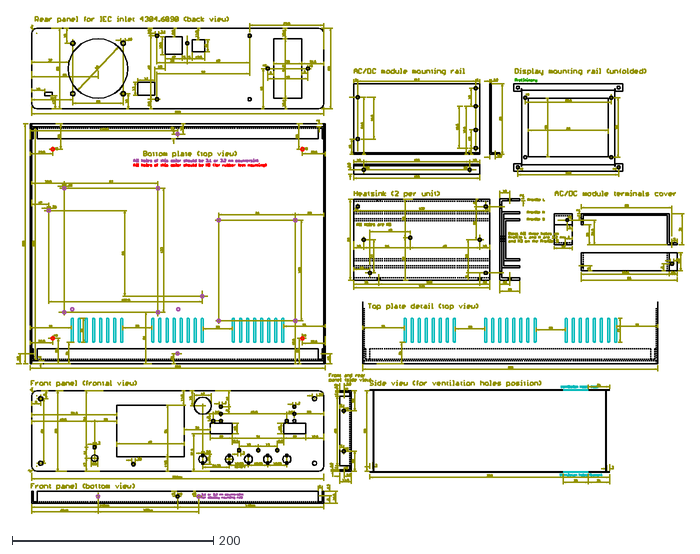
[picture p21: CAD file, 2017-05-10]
Mechanical/EEZ PSU H24005 enclosure r5B12.dxf
663.5 x 494.2

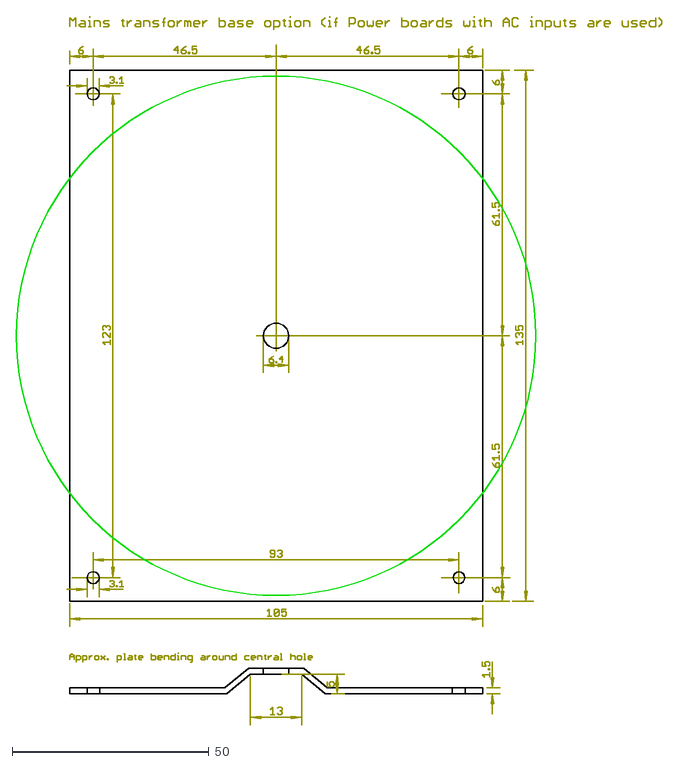
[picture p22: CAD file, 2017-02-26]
Mechanical/EEZ PSU H24005 trafo base.dxf
164.0 x 180.2

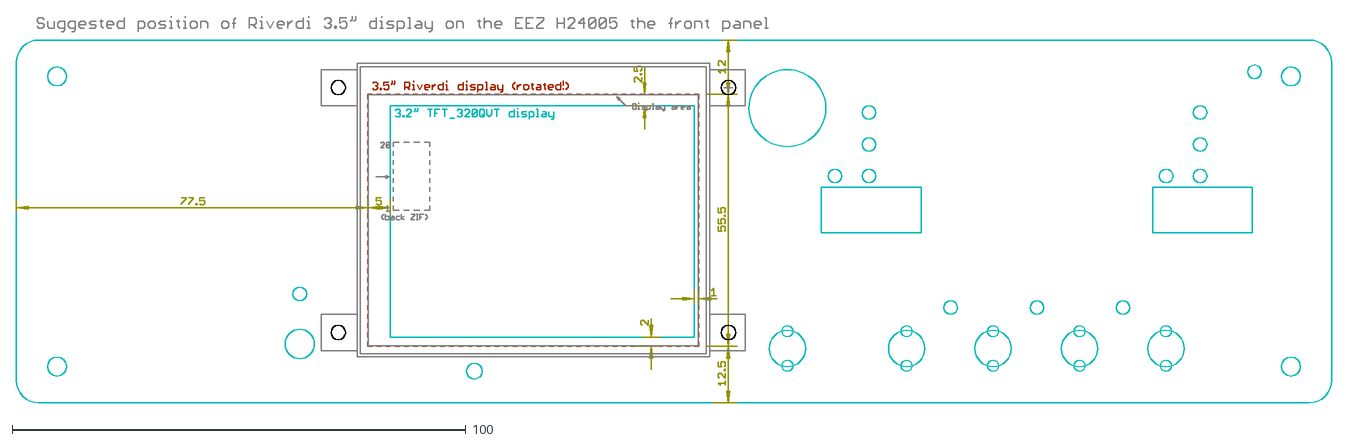
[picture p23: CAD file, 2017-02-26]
Mechanical/EEZ PSU H24005 dual display hole.dxf
290.0 x 85.3

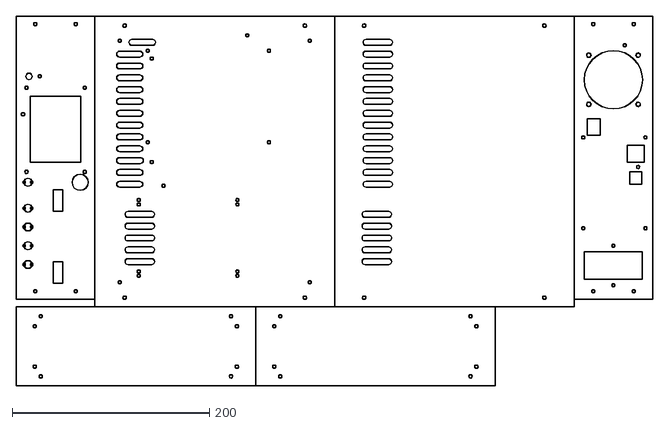
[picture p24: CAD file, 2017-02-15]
Mechanical/EEZ PSU H24005 enclosure r5B12 (for 4mm acryl).dxf
646.0 x 375.0

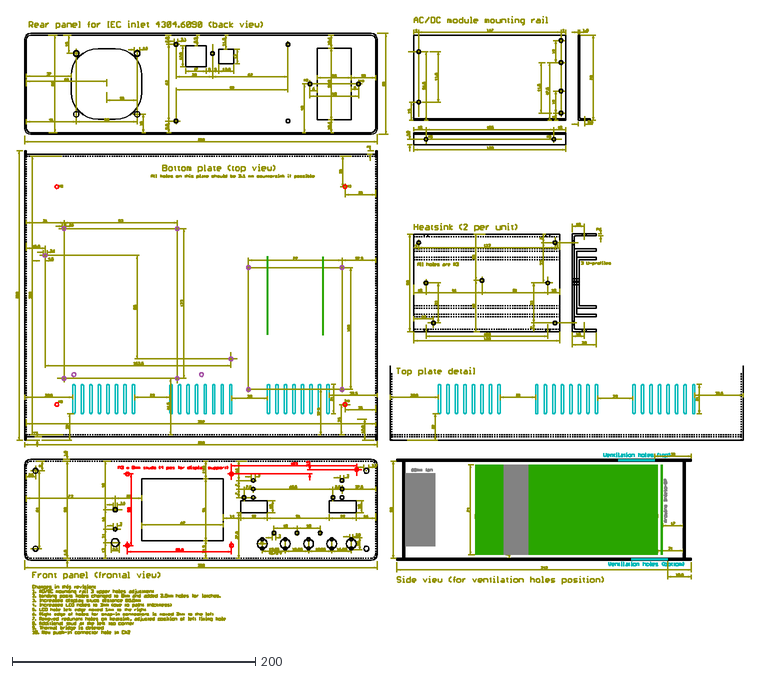
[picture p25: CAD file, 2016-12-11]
Mechanical/EEZ PSU H24005 enclosure r5B11.dxf
597.5 x 508.1

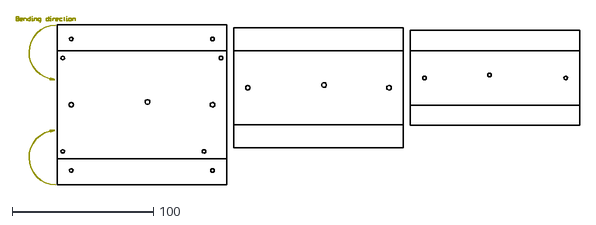
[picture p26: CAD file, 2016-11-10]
Mechanical/EEZ PSU H24005 heatsink unfolded.dxf
399.0 x 119.4

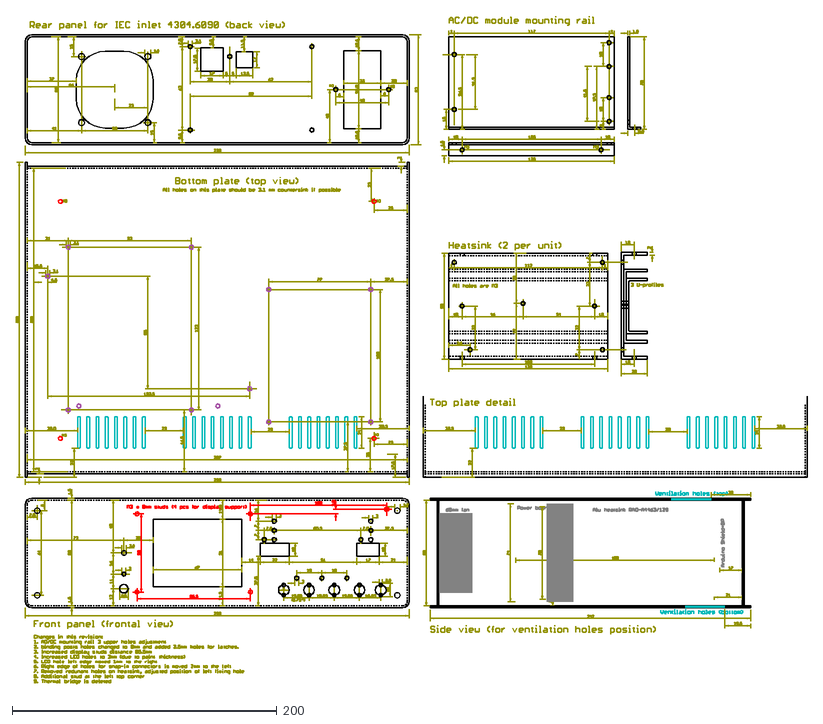
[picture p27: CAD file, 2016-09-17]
Mechanical/EEZ PSU H24005 enclosure r5.1.dxf
597.5 x 504.4

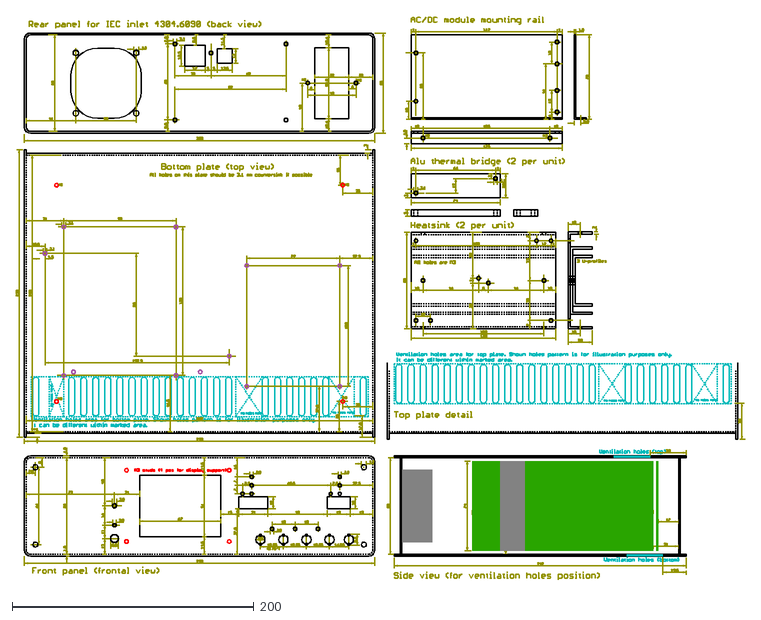
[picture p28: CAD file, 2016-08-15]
Mechanical/EEZ PSU H24005 enclosure r4.6.dxf
603.5 x 466.7

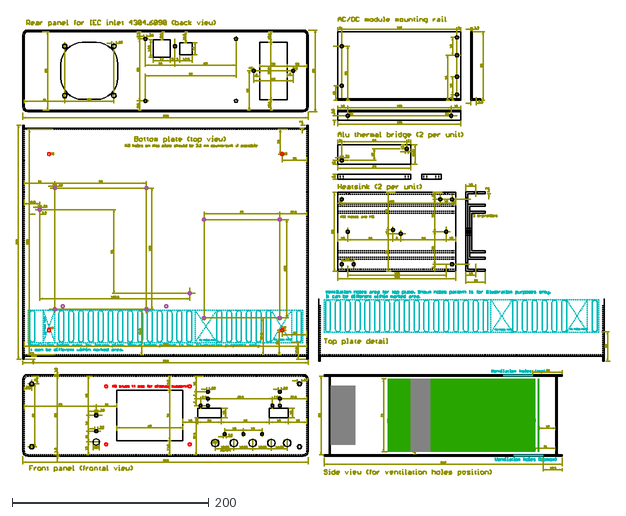
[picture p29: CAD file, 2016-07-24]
Mechanical/EEZ PSU H24005 enclosure r4.5.dxf
603.5 x 466.7

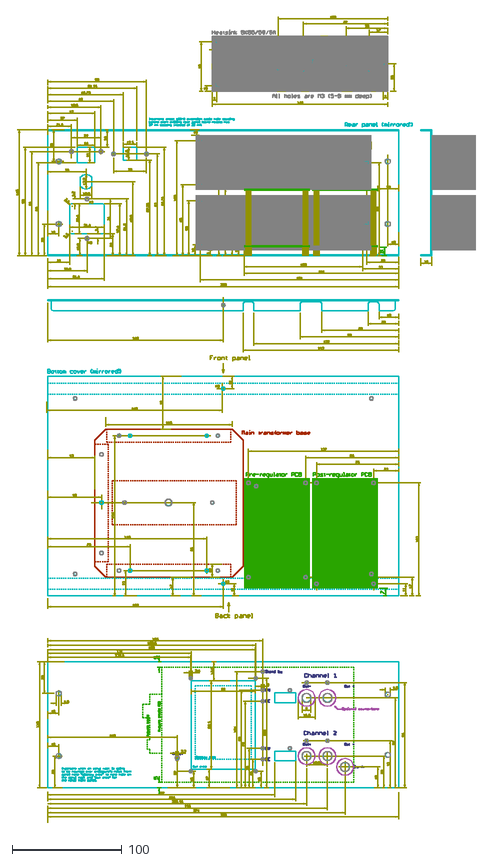
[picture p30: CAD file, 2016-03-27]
Mechanical/EEZ PSU enclosure (Economica 320x200x115, Arduino shield r1b13).dxf
418.6 x 735.6

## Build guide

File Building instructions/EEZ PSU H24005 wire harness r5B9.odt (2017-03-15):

# EEZ PSU H24005 wire harness

- Ethernet cable
- Cooling fan cable
- AUX temperature sensor cable
- AC switch patch cables
- Cable set #1
- Cable set #2
- Pre-assembled cables
- BOM

## Ethernet cable

Total length | 250 (± 5) mm
Type | 4 pairs Ethernet, stranded wire
TME | HELUKAT100-FTP-FP (http://www.tme.eu/en/details/helukat100-ftp-fp/telecommunication-cables/helukabel/80055/) or e.g. cut CA00600.00C01 (http://www.tme.eu/en/details/ca00600.00c01/rj45-cables/belden/) to size
Farnell | 1602385 (http://export.farnell.com/draka/900221va0000fe0100/cable-patch-5e-utp-grey-100m/dp/1602385) or e.g. cut 1734894 (http://export.farnell.com/pro-signal/ps11029/patch-lead-5e-0-5m-grey/dp/1734894) to size
Connectors
Side A | X8 | Side B | X18
Housing type | Receptacle, 0.1” | Housing type | See side A
TME | NSR-08 (http://www.tme.eu/en/details/nsr-08/pin-headers/ninigi/) | TME | See side A
Farnell | 865667 (http://export.farnell.com/harwin/m20-1060800/crimp-housing-8way/dp/865667) | Farnell | See side A
Pin: | Female | Pin | See side A
Pin quantity | 8 | Pin quantity | 7
TME | NDR-T (http://www.tme.eu/en/details/ndr-t/pin-headers/ninigi/) | TME | See side A
Farnell | 1022219 (http://export.farnell.com/harwin/m20-1180042/crimp-socket-gold-22-30awg-pk100/dp/1022219) | Farnell | See side A

Wiring

Name | Position | Color / description | Position | Color / description
LED link | 1 | Brown-white | 1 | Brown-white
LED act | 2 | Brown | 2 | Brown
Shield | 3 | Blue-white | 3 | NOT CONNECTED
RX+ | 4 | Orange-white | 4 | Orange-white
RX- | 5 | Orange | 5 | Orange
TX+ | 6 | Green-white | 6 | Green-white
TX- | 7 | Green | 7 | Green
+3.3V | 8 | Blue | 8 | Blue

Picture

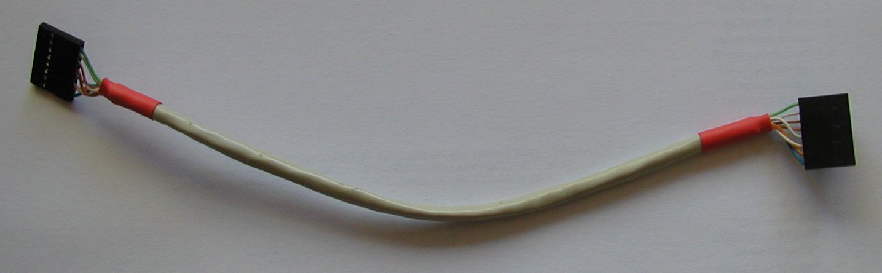
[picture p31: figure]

(http://www.envox.hr/eez/images/ethernet_cable.jpg)

## Cooling fan cable

Total length | 100 (± 5) mm
Type | 3 wire, already mounted on the cooling fan
Fan: | TME: MB60251V1-G99 (http://www.tme.eu/en/details/mb60251v1-g99/dc12v-fans/sunon/mb60251v1-000u-g99/)
Connectors
Side A | X6 | Side B | N/A
Housing type | Receptacle, 0.1” | Housing type | N/A
TME | MX-6471-031 (http://www.tme.eu/en/details/mx-6471-031/raster-signal-connectors-254mm/molex/022012035-22-01-2035-6471-03i/) | TME | N/A
Farnell | 143127 (http://export.farnell.com/molex/22-01-2035/crimp-housing-2-54mm-3way/dp/143127) | Farnell | N/A
Pin | Female | Pin | N/A
Pin quantity | 3 | Pin quantity | 0
TME | MX-0850-0114 (http://www.tme.eu/en/details/mx-0850-0114/raster-signal-connectors-254mm/molex/008500114-08-50-0114-2759-p909l/) | TME | N/A
Farnell | 2063734 (http://export.farnell.com/molex/08-50-0113/contact-crimp-terminal-30-22awg/dp/2063734) | Farnell | N/A
Additional info
Fan is already equipped with cable that has to be cut to size and terminated with connector

Wiring

Name | Position | Color / description
12 Vdc | 1 | Red
GND | 2 | Black
Sense | 3 | Yellow

Picture

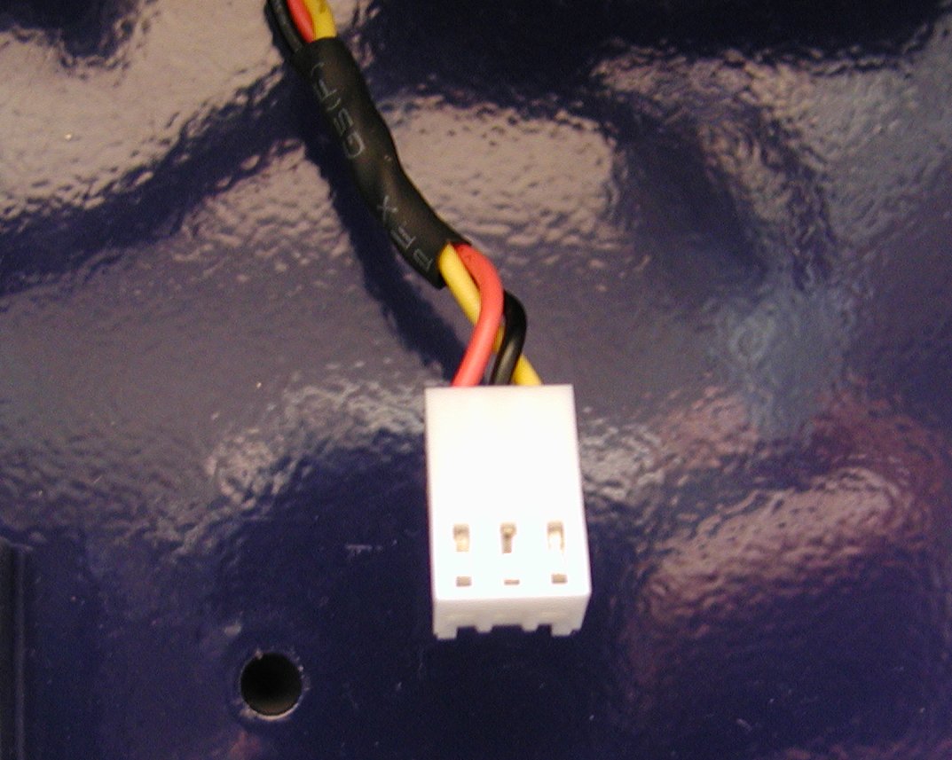
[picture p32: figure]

(http://www.envox.hr/eez/images/fan_connector.jpg)

## AUX temperature sensor cable

Total length | 145 (± 5) mm
Type | Max. 0.35 mm² singe wire, stranded
TME | E.g. brown: LGY0.35/25-BR (http://www.tme.eu/en/details/lgy0.35_25-br/single-core-cable-strand/bq-cable/) (or any other color)
Farnell | E.g. brown: 2425402 (http://export.farnell.com/pro-power/mc6a-7-0-2t2-bn-100/equipment-wire-0-22mm2-brown-per/dp/2425402) (0.22 mm²)
NTC | TME: NTCLE100E3103JB0 (http://www.tme.eu/en/details/ntcle100e3103jb0/tht-measurement-ntc-thermistors/vishay/), Farnell: 1187031 (http://export.farnell.com/vishay/ntcle100e3103jb0/thermistor-10k-5-ntc-rad/dp/1187031)
Wire | TME: LGY0.35/25-BR (http://www.tme.eu/en/details/lgy0.35_25-br/single-core-cable-strand/bq-cable/), Farnell:
Connectors
Side A | X17 | Side B | N/A
Housing type | Receptacle 0.1” | Housing type | N/A
TME | MX-6471-021 (http://www.tme.eu/en/details/mx-6471-021/raster-signal-connectors-254mm/molex/022012025-22-01-2025-6471-02i/) | TME | N/A
Farnell | 143126 (http://export.farnell.com/molex/22-01-2025/crimp-housing-2-54mm-2way/dp/143126) | Farnell | N/A
Pin | Female | Pin | N/A
Pin quantity | 2 | Pin quantity | 0
TME | MX-0850-0114 (http://www.tme.eu/en/details/mx-0850-0114/raster-signal-connectors-254mm/molex/008500114-08-50-0114-2759-p909l/) | TME | N/A
Farnell | 2063734 (http://export.farnell.com/molex/08-50-0113/contact-crimp-terminal-30-22awg/dp/2063734) | Farnell | N/A
Additional info
The temperature sensor is already equipped with cable that has to be terminated with connector

Wiring

Name | Position | Color / description
MCU_VCC | 1 | Any color
NTC | 2 | Any color

Picture

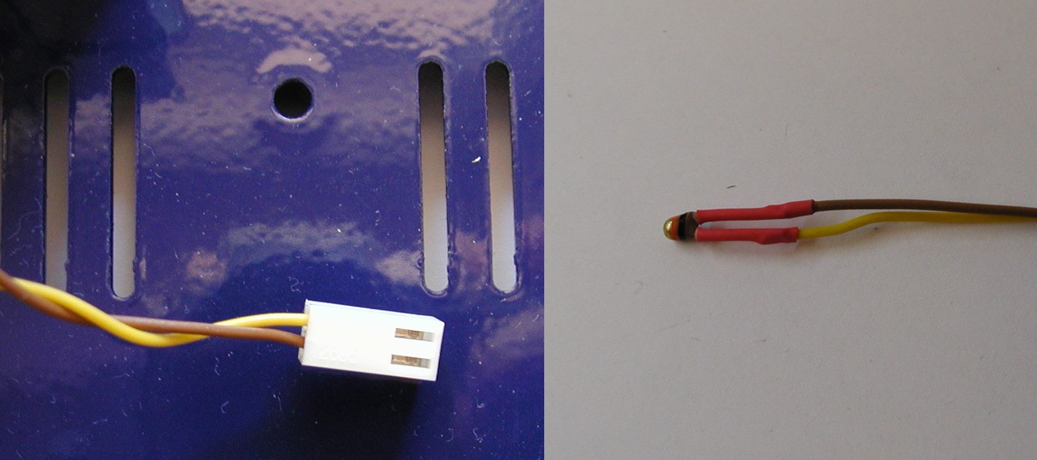
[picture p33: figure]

(http://www.envox.hr/eez/images/temp_sensor2.jpg)

## AC switch patch cables

Total length | 45 (± 5) mm
Type | 0.75 mm² singe wire, stranded, min. 250 VAC
TME | Brown: LGY0.75/25-BR (http://www.tme.eu/en/details/lgy0.75_25-br/single-core-cable-strand/bq-cable/), Blue: LGY0.75/25-BL (http://www.tme.eu/en/details/lgy0.75_25-bl/single-core-cable-strand/bq-cable/)
Farnell | Brown: 2528103 (http://export.farnell.com/pro-power/pp001205/tri-rated-wire-0-75mm2-brown-1m/dp/2528103), Blue: 2528092 (http://export.farnell.com/pro-power/pp001196/tri-rated-wire-0-75mm2-blue-1m/dp/2528092)
Connectors
Side A | AC output | Side B | AC Switch input
Pin | Female quick disconnect | Pin | See side A
Pin quantity | 2 | Pin quantity | See side A
TME | BM01148 (http://www.tme.eu/en/details/bm01148/non-insulated-terminals/bm-group/bm-01148/) | TME | See side A
Farnell | 3625424 (http://export.farnell.com/jst-japan-solderless-terminals/sto-1-0t-187n-8/terminal-female-4-8x0-8mm/dp/3625424) | Farnell | See side A
Additional info
Required for Schurter 4304.6090 (http://www.tme.eu/en/details/4304.6090/ac-power-connectors/schurter/) IEC inlet (C14, 6765, 10A)

Wiring1

Name | Position | Color / description | Position | Color / description
Line | 1 | Brown | 1 | Brown

Wiring2

Name | Position | Color / description | Position | Color / description
Neutral | 1 | Blue | 1 | Blue

Picture

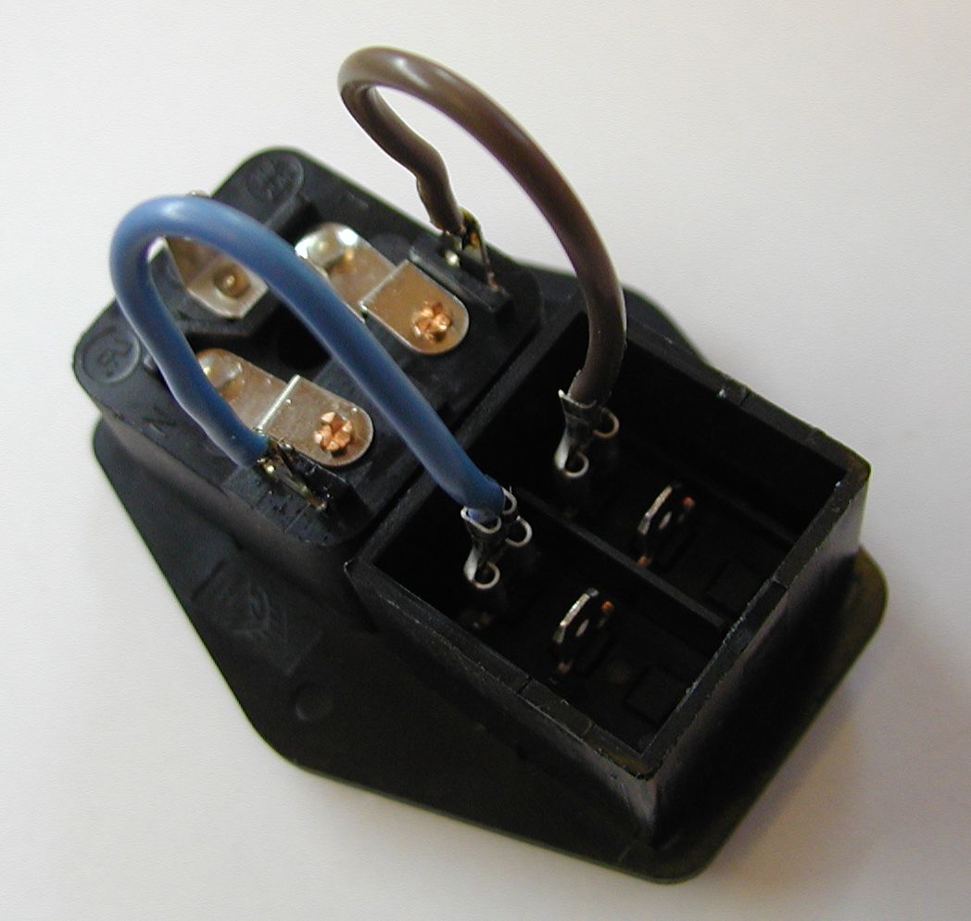
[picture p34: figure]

(http://www.envox.hr/eez/images/ac_inlet_wiring.jpg)

## Cable set #1

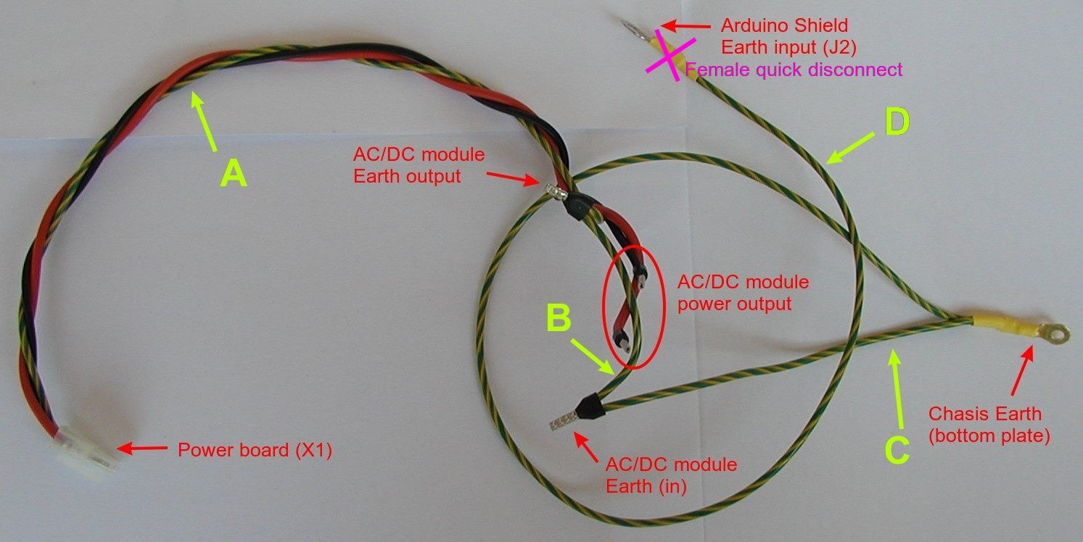
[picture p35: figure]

(http://www.envox.hr/eez/images/cable_set1_rev2.jpg)

### Section A: Power board X1 cable

Length | 400 (± 5) mm
Type | 0.75 mm² singe wire, stranded, min. 250 VAC
TME | Red: LGY0.75/25-RD (http://www.tme.eu/en/details/lgy0.75_25-rd/single-core-cable-strand/bq-cable/), Black: LGY0.75/25-BK (http://www.tme.eu/en/details/lgy0.75_25-bk/single-core-cable-strand/bq-cable/) Green-Yellow: LGY0.75/25-YL/GR (http://www.tme.eu/en/details/lgy0.75_25-yl_gr/single-core-cable-strand/bq-cable/)
Farnell | Red: 2528175 (http://export.farnell.com/pro-power/pp001270/tri-rated-wire-0-75mm2-red-1m/dp/2528175), Black: 2528082 (http://export.farnell.com/pro-power/pp001186/tri-rated-wire-0-75mm2-black-1m/dp/2528082), Green-Yellow: 2528140 (http://export.farnell.com/pro-power/pp001239/tri-rated-wire-0-75mm2-grn-yellow/dp/2528140)
Connectors
Side A | Power board X1 (Ch2) | Side B | AC/DC module power output
Housing type | Male, Mini-Fit Jr. | Housing type | Ferrule, single wire
TME | MX-5557-03R2 (http://www.tme.eu/en/details/mx-5557-03r2/raster-signal-connectors-420mm/molex/039014030-39-01-4030-5557-03r2/) | TME | H0.75/14D/GY (http://www.tme.eu/en/details/h0.75_14d_gy/bootlace-ferrules/weidmuller/9019040000-h07514d-gr/)
Farnell | 9963480 (http://export.farnell.com/molex/39-01-4030/crimp-housing-rcpt-sil-3way-mini/dp/9963480) | Farnell | 841195 (http://export.farnell.com/weidmuller/h0-75-14/ferrule-insulated-0-75mm-white/dp/841195)
Pin | Female | Quantity | 2
Pin quantity | 3 | Housing type | Ferrule, twin entry
TME | MX-5556-T3L (http://www.tme.eu/en/details/mx-5556-t3l/raster-signal-connectors-420mm/molex/039000078-39-00-0078-5556t3l/) | TME | H0.75/15D2/GY (http://www.tme.eu/en/details/h0.75_15d2_gy/bootlace-ferrules/weidmuller/9037410000-h07514d-zh-gr/)
Farnell | 9732675 (http://export.farnell.com/molex/39-00-0078/crimp-socket-16awg-pk100/dp/9732675) | Farnell | 1121751 (http://export.farnell.com/weidmuller/9037410000/ferrule-twin-entry-0-75mm/dp/1121751)
| | Quantity | 1

Wiring

Name | Position | Color / description | Position | Color / description
Earth | 1 | Green-Yellow | N/A | Ferrule, twin entry
Vin- | 2 | Black | N/A | Ferrule
Vin+ | 3 | Red | N/A | Ferrule

### Section B: AC/DC module Earth

Length | 70 (± 1) mm
Type | 0.75 mm² singe wire, stranded, min. 250 VAC
TME | LGY0.75/25-YL/GR (http://www.tme.eu/en/details/lgy0.75_25-yl_gr/single-core-cable-strand/bq-cable/)
Farnell | 2528140 (http://export.farnell.com/pro-power/pp001239/tri-rated-wire-0-75mm2-grn-yellow/dp/2528140)
Connectors
Side A | AC/DC module Earth output | Side B | AC/DC module Earth (in)
Housing type | Use twin entry ferrule, See B side, Section A | Housing type | Ferrule, twin entry
| | TME | H0.75/15D2/GY (http://www.tme.eu/en/details/h0.75_15d2_gy/bootlace-ferrules/weidmuller/9037410000-h07514d-zh-gr/)
| | Farnell | 1121751 (http://export.farnell.com/weidmuller/9037410000/ferrule-twin-entry-0-75mm/dp/1121751)
| | Quantity | 1

### Section C: Chassis Earth

Length: | 170 (± 5) mm
Type: | 0.75 mm² singe wire, stranded, min. 250 VAC
TME | LGY0.75/25-YL/GR (http://www.tme.eu/en/details/lgy0.75_25-yl_gr/single-core-cable-strand/bq-cable/)
Farnell | 2528140 (http://export.farnell.com/pro-power/pp001239/tri-rated-wire-0-75mm2-grn-yellow/dp/2528140)
Connectors
Side A | AC/DC module Earth (in) | Side B | Chassis Earth (bottom plate)
Housing type | Use twin entry ferrule, See B side, Section B | Housing type | Non-insulated, Ring terminal, 3 mm
| | TME | BM 91103 (http://www.tme.eu/en/details/bm91103/non-insulated-terminals/bm-group/bm-91103/)
| | Farnell | 7356528 (http://export.farnell.com/jst-japan-solderless-terminals/lrb-1-0t-m3/crimp-terminal-ring-m3/dp/7356528)
| | Quantity | 1

### Section D: Arduino Shield Earth

Length: | 500 (± 5) mm
Type: | 0.75 mm² singe wire, stranded, min. 250 VAC
TME | LGY0.75/25-YL/GR (http://www.tme.eu/en/details/lgy0.75_25-yl_gr/single-core-cable-strand/bq-cable/)
Farnell | 2528140 (http://export.farnell.com/pro-power/pp001239/tri-rated-wire-0-75mm2-grn-yellow/dp/2528140)
Connectors
Side A | Chassis Earth (bottom plate) | Side B | Arduino Shield Earth input (J2)
Housing type | Use ring terminal, See B side, Section C | Housing type | Female quick disconnect
| | TME | 1
| | Farnell | BM01148 (http://www.tme.eu/en/details/bm01148/non-insulated-terminals/bm-group/bm-01148/)
| | Quantity | 3625424 (http://export.farnell.com/jst-japan-solderless-terminals/sto-1-0t-187n-8/terminal-female-4-8x0-8mm/dp/3625424)

## Cable set #2

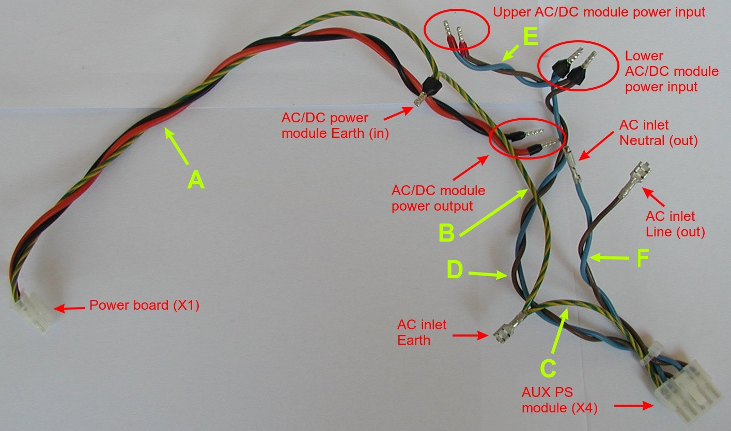
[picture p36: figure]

(http://www.envox.hr/eez/images/cable_set2.jpg)

### Section A: Power board X1 cable

Length | 330 (± 5) mm
Type | 0.75 mm² singe wire, stranded, min. 250 VAC
TME | Red: LGY0.75/25-RD (http://www.tme.eu/en/details/lgy0.75_25-rd/single-core-cable-strand/bq-cable/), Black: LGY0.75/25-BK (http://www.tme.eu/en/details/lgy0.75_25-bk/single-core-cable-strand/bq-cable/) Green-Yellow: LGY0.75/25-YL/GR (http://www.tme.eu/en/details/lgy0.75_25-yl_gr/single-core-cable-strand/bq-cable/)
Farnell | Red: 2528175 (http://export.farnell.com/pro-power/pp001270/tri-rated-wire-0-75mm2-red-1m/dp/2528175), Black: 2528082 (http://export.farnell.com/pro-power/pp001186/tri-rated-wire-0-75mm2-black-1m/dp/2528082), Green-Yellow: 2528140 (http://export.farnell.com/pro-power/pp001239/tri-rated-wire-0-75mm2-grn-yellow/dp/2528140)
Connectors
Side A | Power board X1 (Ch1) | Side B | AC/DC module power output
Housing type | Male, Mini-Fit Jr. | Housing type | Ferrule, single wire
TME | MX-5557-03R2 (http://www.tme.eu/en/details/mx-5557-03r2/raster-signal-connectors-420mm/molex/039014030-39-01-4030-5557-03r2/) | TME | H0.75/14D/GY (http://www.tme.eu/en/details/h0.75_14d_gy/bootlace-ferrules/weidmuller/9019040000-h07514d-gr/)
Farnell | 9963480 (http://export.farnell.com/molex/39-01-4030/crimp-housing-rcpt-sil-3way-mini/dp/9963480) | Farnell | 841195 (http://export.farnell.com/weidmuller/h0-75-14/ferrule-insulated-0-75mm-white/dp/841195)
Pin | Female | Quantity | 2
Pin quantity | 3 | Housing type | Ferrule, twin entry
TME | MX-5556-T3L (http://www.tme.eu/en/details/mx-5556-t3l/raster-signal-connectors-420mm/molex/039000078-39-00-0078-5556t3l/) | TME | H0.75/15D2/GY (http://www.tme.eu/en/details/h0.75_15d2_gy/bootlace-ferrules/weidmuller/9037410000-h07514d-zh-gr/)
Farnell | 9732675 (http://export.farnell.com/molex/39-00-0078/crimp-socket-16awg-pk100/dp/9732675) | Farnell | 1121751 (http://export.farnell.com/weidmuller/9037410000/ferrule-twin-entry-0-75mm/dp/1121751)
| | Quantity | 1

Wiring:

Name | Position | Color / description | Position | Color / description
Earth | 1 | Green-Yellow | N/A | Ferrule, twin entry
Vin- | 2 | Black | N/A | Ferrule
Vin+ | 3 | Red | N/A | Ferrule

### Section B: AC/DC module Earth

Length | 150 (± 5) mm
Type | 0.75 mm² singe wire, stranded, min. 250 VAC
TME | LGY0.75/25-YL/GR (http://www.tme.eu/en/details/lgy0.75_25-yl_gr/single-core-cable-strand/bq-cable/)
Farnell | 2528140 (http://export.farnell.com/pro-power/pp001239/tri-rated-wire-0-75mm2-grn-yellow/dp/2528140)
Connectors
Side A | AC/DC power module Earth (in) | Side B | AC inlet Earth
Housing type | Use twin entry ferrule, See B side from Section A | Housing type | Female quick disconnect
| | Quantity | 1
| | TME | BM01148 (http://www.tme.eu/en/details/bm01148/non-insulated-terminals/bm-group/bm-01148/)
| | Farnell | 3625424 (http://export.farnell.com/jst-japan-solderless-terminals/sto-1-0t-187n-8/terminal-female-4-8x0-8mm/dp/3625424)

### Section C: AUX PS module Earth

Length | 150 (± 5) mm
Type | 0.75 mm² singe wire, stranded, min. 250 VAC
TME | LGY0.75/25-YL/GR (http://www.tme.eu/en/details/lgy0.75_25-yl_gr/single-core-cable-strand/bq-cable/)
Farnell | 2528140 (http://export.farnell.com/pro-power/pp001239/tri-rated-wire-0-75mm2-grn-yellow/dp/2528140)
Connectors
Side A | AC inlet Earth | Side B | AUX PS module (X4)
Housing type | Use Female quick disconnect terminal, See B side, Section B | Housing type | Male, Mini-Fit Jr.
| | TME | MX-5557-05R2 (http://www.tme.eu/en/details/mx-5557-05r2/raster-signal-connectors-420mm/molex/039014050-39-01-4050-5557-05r2/)
| | Farnell | 9963502 (http://export.farnell.com/molex/39014050/crimp-housing-rcpt-sil-5way-mini/dp/9963502)
| | Pin | Female
| | Pin quantity | 1
| | TME | MX-5556-T3L (http://www.tme.eu/en/details/mx-5556-t3l/raster-signal-connectors-420mm/molex/039000078-39-00-0078-5556t3l/)
| | Farnell | 9732675 (http://export.farnell.com/molex/39-00-0078/crimp-socket-16awg-pk100/dp/9732675)

Wiring:

Name | Position | Color / description | Position | Color / description
- | - | Female quick disconnect | 1 | Earth

### Section D: Lower AC/DC module power input

Length | 200 (± 5) mm
Type | 0.75 mm² singe wire, stranded, min. 250 VAC
TME | Brown: LGY0.75/25-BR (http://www.tme.eu/en/details/lgy0.75_25-br/single-core-cable-strand/bq-cable/), Blue: LGY0.75/25-BL (http://www.tme.eu/en/details/lgy0.75_25-bl/single-core-cable-strand/bq-cable/)
Farnell | Brown: 2528103 (http://export.farnell.com/pro-power/pp001205/tri-rated-wire-0-75mm2-brown-1m/dp/2528103), Blue: 2528092 (http://export.farnell.com/pro-power/pp001196/tri-rated-wire-0-75mm2-blue-1m/dp/2528092)
Connectors
Side A | AUX PS module (X4) | Side B | Lower AC/DC module power input
Housing type | See Side B, Section C | Housing type | Ferrule, twin entry
TME | - | TME | H0.75/15D2/GY (http://www.tme.eu/en/details/h0.75_15d2_gy/bootlace-ferrules/weidmuller/9037410000-h07514d-zh-gr/)
Farnell | - | Farnell | 1121751 (http://export.farnell.com/weidmuller/9037410000/ferrule-twin-entry-0-75mm/dp/1121751)
Pin | Female | Quantity | 2
Pin quantity | 2
TME | MX-5556-T3L (http://www.tme.eu/en/details/mx-5556-t3l/raster-signal-connectors-420mm/molex/039000078-39-00-0078-5556t3l/) | | (http://www.tme.eu/en/details/mx-5556-t3l/raster-signal-connectors-420mm/molex/039000078-39-00-0078-5556t3l/)
Farnell | 9732675 (http://export.farnell.com/molex/39-00-0078/crimp-socket-16awg-pk100/dp/9732675)

Wiring:

Name | Position | Color / description | Position | Color / description
Neutral | 4 | Blue | N/A | Ferrule, twin entry
Line | 5 | Brown | N/A | Ferrule, twin entry

### Section E: Upper AC/DC module power input

Length | 70 (± 1) mm
Type | 0.75 mm² singe wire, stranded, min. 250 VAC
TME | Brown: LGY0.75/25-BR (http://www.tme.eu/en/details/lgy0.75_25-br/single-core-cable-strand/bq-cable/), Blue: LGY0.75/25-BL (http://www.tme.eu/en/details/lgy0.75_25-bl/single-core-cable-strand/bq-cable/)
Farnell | Brown: 2528103 (http://export.farnell.com/pro-power/pp001205/tri-rated-wire-0-75mm2-brown-1m/dp/2528103), Blue: 2528092 (http://export.farnell.com/pro-power/pp001196/tri-rated-wire-0-75mm2-blue-1m/dp/2528092)
Connectors
Side A | Lower AC/DC module power input | Side B | Upper AC/DC module power input
Housing type | Use twin entry ferrule, See B side, Section D | Housing type | Ferrule, single wire
| | TME | H0.75/14D/GY (http://www.tme.eu/en/details/h0.75_14d_gy/bootlace-ferrules/weidmuller/9019040000-h07514d-gr/)
| | Farnell | 1121751 (http://export.farnell.com/weidmuller/9037410000/ferrule-twin-entry-0-75mm/dp/1121751)
| | Quantity | 2

### Section F: AUX PS module power input

Length | 110 (± 5) mm
Type | 0.75 mm² singe wire, stranded, min. 250 VAC
TME | Brown: LGY0.75/25-BR (http://www.tme.eu/en/details/lgy0.75_25-br/single-core-cable-strand/bq-cable/), Blue: LGY0.75/25-BL (http://www.tme.eu/en/details/lgy0.75_25-bl/single-core-cable-strand/bq-cable/)
Farnell | Brown: 2528103 (http://export.farnell.com/pro-power/pp001205/tri-rated-wire-0-75mm2-brown-1m/dp/2528103), Blue: 2528092 (http://export.farnell.com/pro-power/pp001196/tri-rated-wire-0-75mm2-blue-1m/dp/2528092)
Connectors
Side A | AUX PS module (X4) | Side B | Lower AC/DC module power input
Housing type | See Side B, Section C | Housing type | Female quick disconnect
TME | - | TME | BM01148 (http://www.tme.eu/en/details/bm01148/non-insulated-terminals/bm-group/bm-01148/)
Farnell | - | Farnell | 3625424 (http://export.farnell.com/jst-japan-solderless-terminals/sto-1-0t-187n-8/terminal-female-4-8x0-8mm/dp/3625424)
Pin | Female | Quantity | 2
Pin quantity | 2
TME | MX-5556-T3L (http://www.tme.eu/en/details/mx-5556-t3l/raster-signal-connectors-420mm/molex/039000078-39-00-0078-5556t3l/) | | (http://www.tme.eu/en/details/mx-5556-t3l/raster-signal-connectors-420mm/molex/039000078-39-00-0078-5556t3l/)
Farnell | 9732675 (http://export.farnell.com/molex/39-00-0078/crimp-socket-16awg-pk100/dp/9732675)

Wiring:

Name | Position | Color / description | Position | Color / description
Neutral | 2 | Blue | N/A | Female quick disconnect
Line | 3 | Brown | N/A | Female quick disconnect

## Pre-assembled cables

### Arduino shield power cable

Length | 300 mm
Type | Ribbon cable with IDC connectors; 10x28AWG
TME | FC10300-0 (http://www.tme.eu/en/details/fc10300-0/ribbon-cables-with-idc-connectors/amphenol/)
Farnell | N/A

Picture

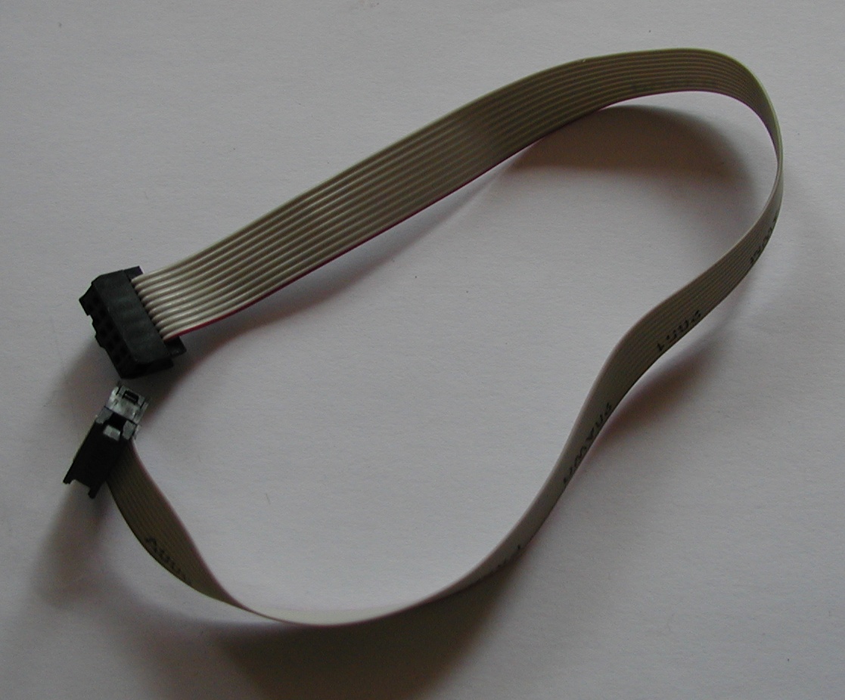
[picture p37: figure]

(http://www.envox.hr/eez/images/idc_cable.jpg)

Pinout:

Name | Position | Description
Gnd | 1 | Ground
Gnd | 2 | Ground
PWR_DIRECT | 3 | Triac control (continuous power)
PWR_SSTART | 4 | Triac control (soft-start)
FAN_SENSE | 5 | Tachometer output
FAN_PWM | 6 | Fan PWM speed control
DOUT2 | 7 | Power relay control
+5V | 8 | +5 V for Arduino Shield
Gnd | 9 | Ground
+5V | 10 | +5 V for Arduino Shield

### Arduino USB cable

Length | 300 or 500 mm
Type | USB Micro to 5-pin receptacle cable
TME | N/A
Farnell | N/A
AliExpress | e.g. High Quality 50CM micro usb 5pin male to 1x 5Pin Female 0.1" USB header PCB motherboard cable (https://www.aliexpress.com/item/Free-Shipping-50CM-micro-usb-5pin-male-to-1x-5Pin-Female-0-1-USB-header-PCB/32233605468.html)


(http://www.envox.hr/eez/images/arduino_usb_cable.png)

Pinout:

Name | Position | Color | Description
VCC | 1 | Red | +5 Vdc
D- | 2 | White | Data -
D+ | 3 | Green | Data +
GND | 4 | Black | Ground
Shield | 5 | Black | Shield

## BOM

Type | Part (Farnell) | Part (TME) | Total
Receptacle | 865667 (http://export.farnell.com/harwin/m20-1060800/crimp-housing-8way/dp/865667) | NSR-08 (http://www.tme.eu/en/details/nsr-08/pin-headers/ninigi/) | 2
Receptacle | 143127 (http://export.farnell.com/molex/22-01-2035/crimp-housing-2-54mm-3way/dp/143127) | MX-6471-031 (http://www.tme.eu/en/details/mx-6471-031/raster-signal-connectors-254mm/molex/022012035-22-01-2035-6471-03i/) | 1
Receptacle | 143126 (http://export.farnell.com/molex/22-01-2025/crimp-housing-2-54mm-2way/dp/143126) | MX-6471-021 (http://www.tme.eu/en/details/mx-6471-021/raster-signal-connectors-254mm/molex/022012025-22-01-2025-6471-02i/) | 1
Receptacle Mini-Fit Jr. | 9963480 (http://export.farnell.com/molex/39-01-4030/crimp-housing-rcpt-sil-3way-mini/dp/9963480) | MX-5557-03R2 (http://www.tme.eu/en/details/mx-5557-03r2/raster-signal-connectors-420mm/molex/039014030-39-01-4030-5557-03r2/) | 2
Receptacle Mini-Fit Jr. | 9963502 (http://export.farnell.com/molex/39014050/crimp-housing-rcpt-sil-5way-mini/dp/9963502) | MX-5557-05R2 (http://www.tme.eu/en/details/mx-5557-05r2/raster-signal-connectors-420mm/molex/039014050-39-01-4050-5557-05r2/) | 1
Pin | 1022219 (http://export.farnell.com/harwin/m20-1180042/crimp-socket-gold-22-30awg-pk100/dp/1022219) | NDR-T (http://www.tme.eu/en/details/ndr-t/pin-headers/ninigi/) | 15
Pin | 2063734 (http://export.farnell.com/molex/08-50-0113/contact-crimp-terminal-30-22awg/dp/2063734) | MX-0850-0114 (http://www.tme.eu/en/details/mx-0850-0114/raster-signal-connectors-254mm/molex/008500114-08-50-0114-2759-p909l/) | 5
Pin | 9732675 (http://export.farnell.com/molex/39-00-0078/crimp-socket-16awg-pk100/dp/9732675) | MX-5556-T3L (http://www.tme.eu/en/details/mx-5556-t3l/raster-signal-connectors-420mm/molex/039000078-39-00-0078-5556t3l/) | 11
Female quick disconnect | 3625424 (http://export.farnell.com/jst-japan-solderless-terminals/sto-1-0t-187n-8/terminal-female-4-8x0-8mm/dp/3625424) | BM01148 (http://www.tme.eu/en/details/bm01148/non-insulated-terminals/bm-group/bm-01148/) | 6
Ferrule | 841195 (http://export.farnell.com/weidmuller/h0-75-14/ferrule-insulated-0-75mm-white/dp/841195) | H0.75/14D/GY (http://www.tme.eu/en/details/h0.75_14d_gy/bootlace-ferrules/weidmuller/9019040000-h07514d-gr/) | 6
Ferrule, twin entry | 1121751 (http://export.farnell.com/weidmuller/9037410000/ferrule-twin-entry-0-75mm/dp/1121751) | H0.75/15D2/GY (http://www.tme.eu/en/details/h0.75_15d2_gy/bootlace-ferrules/weidmuller/9037410000-h07514d-zh-gr/) | 5
Ring terminal | 7356528 (http://export.farnell.com/jst-japan-solderless-terminals/lrb-1-0t-m3/crimp-terminal-ring-m3/dp/7356528) | BM 91103 (http://www.tme.eu/en/details/bm91103/non-insulated-terminals/bm-group/bm-91103/) | 1
Cat5e cable | 1602385 (http://export.farnell.com/draka/900221va0000fe0100/cable-patch-5e-utp-grey-100m/dp/1602385) | HELUKAT100-FTP-FP (http://www.tme.eu/en/details/helukat100-ftp-fp/telecommunication-cables/helukabel/80055/) | 0.25 m
0.75 cm² cable (Brown) | 2528103 (http://export.farnell.com/pro-power/pp001205/tri-rated-wire-0-75mm2-brown-1m/dp/2528103) | LGY0.75/25-BR (http://www.tme.eu/en/details/lgy0.75_25-br/single-core-cable-strand/bq-cable/) | 0.47 m
0.75 cm² cable (Blue) | 2528092 (http://export.farnell.com/pro-power/pp001196/tri-rated-wire-0-75mm2-blue-1m/dp/2528092) | LGY0.75/25-BL (http://www.tme.eu/en/details/lgy0.75_25-bl/single-core-cable-strand/bq-cable/) | 0.47 m
0.75 cm² cable (Red) | 2528175 (http://export.farnell.com/pro-power/pp001270/tri-rated-wire-0-75mm2-red-1m/dp/2528175) | LGY0.75/25-RD (http://www.tme.eu/en/details/lgy0.75_25-rd/single-core-cable-strand/bq-cable/) | 0.73 m
0.75 cm² cable (Black) | 2528082 (http://export.farnell.com/pro-power/pp001186/tri-rated-wire-0-75mm2-black-1m/dp/2528082) | LGY0.75/25-BK (http://www.tme.eu/en/details/lgy0.75_25-bk/single-core-cable-strand/bq-cable/) | 0.73 m
0.75 cm² cable (Yellow-Green) | 2528140 (http://export.farnell.com/pro-power/pp001239/tri-rated-wire-0-75mm2-grn-yellow/dp/2528140) | LGY0.75/25-YL/GR (http://www.tme.eu/en/details/lgy0.75_25-yl_gr/single-core-cable-strand/bq-cable/) | 1.77 m
0.35 cm² cable | 2425402 (http://export.farnell.com/pro-power/mc6a-7-0-2t2-bn-100/equipment-wire-0-22mm2-brown-per/dp/2425402) | LGY0.35/25-BR (http://www.tme.eu/en/details/lgy0.35_25-br/single-core-cable-strand/bq-cable/) | 0.29 m
12 Vdc cooling fan | – | MB60251V1-G99 (http://www.tme.eu/en/details/mb60251v1-g99/dc12v-fans/sunon/mb60251v1-000u-g99/) | 1
NTC | 1187031 (http://export.farnell.com/vishay/ntcle100e3103jb0/thermistor-10k-5-ntc-rad/dp/1187031) | NTCLE100E3103JB0 (http://www.tme.eu/en/details/ntcle100e3103jb0/tht-measurement-ntc-thermistors/vishay/) | 1
IDC ribbon cable | – | FC10300-0 (http://www.tme.eu/en/details/fc10300-0/ribbon-cables-with-idc-connectors/amphenol/) | 0.3 m
USB Micro cable | Search Aliexpress (https://www.aliexpress.com/item/Free-Shipping-50CM-micro-usb-5pin-male-to-1x-5Pin-Female-0-1-USB-header-PCB/32233605468.html) | | 0.5 m

EEZ PSU H24005 wire harness

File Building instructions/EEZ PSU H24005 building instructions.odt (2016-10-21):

# EEZ PSU H24005 Building Instructions (r5B9)

Work in progress

- PCB assembly
- Firmware uploading

## PCB assembly

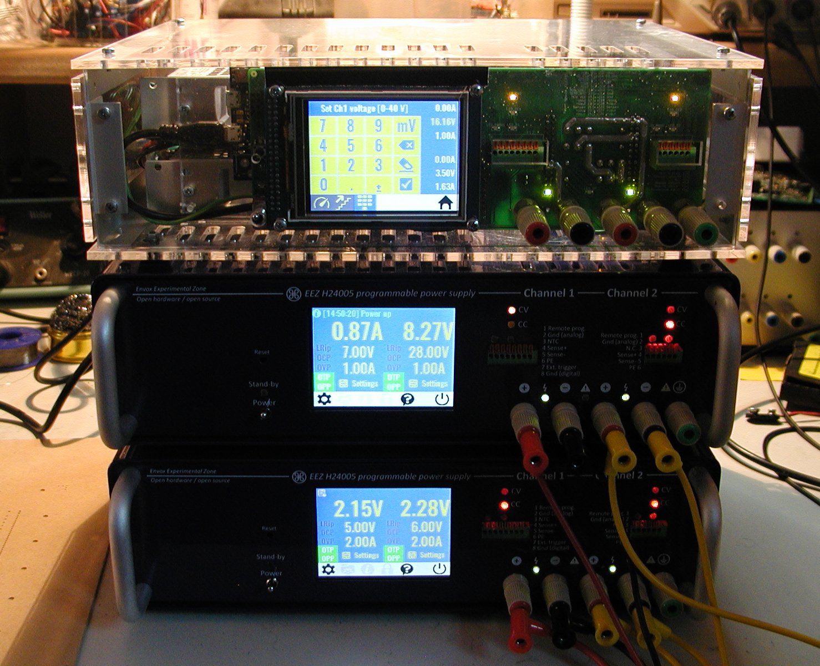
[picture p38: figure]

(http://www.envox.hr/eez/images/h24005_group_photo.jpg)Fig. 1: Stacked assembled EEZ PSU H24005 in acryl and metal enclosures

The PSU has four PCBs where SMT (https://en.wikipedia.org/wiki/Surface-mount_technology) parts are used to the greatest extent. Only connectors and few specialized parts (e.g. power resistor, PCB mounted AC/DC adapter, post-regulator's power mosfet, etc.) are THT (https://en.wikipedia.org/wiki/Through-hole_technology).

SMT parts are selected to be easily mounted with hand soldering and assistance of magnifying glass with light or low magnification microscope. In general, a magnification of x8 to x10 should be more then appropriate for this task. Almost all passive components are of 0805 size and never smaller then 0603. Selected IC packages are SOIC, TSOP, TSSOP and similar that have exposed pins (i.e. no QFN (https://en.wikipedia.org/wiki/Quad_Flat_No-leads_package) or BGA (https://en.wikipedia.org/wiki/Ball_grid_array) package are selected).

Only two ICs (IC1, IC16) that has exposed power tab cannot be simply mounted with soldering iron and need hot air soldering station. That requires different skills but one can find many useful videos on the Internet with instructions how to do that efficiently at home without use of e.g. stencil and reflow owen (https://en.wikipedia.org/wiki/Reflow_soldering).

### Required tools

- Soldering iron with conical sloped tip example (http://www.tme.eu/en/details/wel.et-f/soldering-tips/weller/)
- Hot air soldering station example (http://www.tme.eu/en/details/at850d/hot-air-stations/atten/)
- Solder wire 0.25 mm example (http://www.tme.eu/en/details/sn99c-0.25_0.1/solders-wires/cynel/), and 0.7 mm example (http://www.tme.eu/en/details/brof63-07_01h/solders-wires/broquetas-sl/brofil-63-b21-07mm-100g/) (optionally solder paste, for ICs with exposed power tabs but take into account that its shelf life is very limited even when refrigerated, therefore use small package, example (http://www.tme.eu/en/details/esn62pb36ag_8/solders-pastes/ag-termopasty/))
- Solder wick / desoldering braid example (http://www.tme.eu/en/details/d-ls20/desoldering-wicks/donau/)
- Flux example (http://www.tme.eu/en/details/flux-tk_50/fluxes/ag-termopasty/tk-83/)
- Magnifying glass with light (desktop magnifier with backlight) example (http://www.tme.eu/en/details/lup-19-led/desktop-magnifiers-with-backlight/newbrand/) or microscope example (http://www.tme.eu/en/details/nb-xt3b/microscopes/newbrand/)
- Self-locking tweezers example (http://www.tme.eu/en/details/brn-5-058/precision-tweezers/bernstein/5-058/)
- Set of tweezers example1 (http://www.tme.eu/en/katalog/#cleanParameters=1&searchClick=1&search=NB-ESD14), example2 (http://www.tme.eu/en/details/nb-esd15/esd-tweezers/newbrand/)
- Isopropyl alcohol example (http://www.tme.eu/en/details/ip_1l/cleaning-maintaining-products/) and paper wipes example (http://www.tme.eu/en/details/kim-7558_200/wipes-cleaning-clothes/kimberly-clark/7558/) for cleaning
- PCB holder example (http://www.tme.eu/en/details/sp-holder-1/soldering-devices-others/solder-peak/)

### Test and measurement equipment

The basic tool used for measurement is an oscilloscope. But, if assembling is performed carefully, that no single mistake has been done, (e.g. wrong part value or place, etc.) a simple DMM will be enough to check basic functionality.

During testing and taking measurements please take into account that channel’s negative output (OUT-) is NOT on ground potential. Therefore if you are using multichannel oscilloscope without isolated channels (that is default!) you cannot concurrently connect test probe ground of one channel to the PGND and another one to OUT-. That will interfere with normal operation of CC control loop (IC7, IC8) because the current sense resistor (R69) will be shorted in that way.

### Where to start?

The total number of parts that have to be soldered is almost 800. On the first sight that can easily discourage many, but it's not so bad. First, two most demanding PCBs for power boards are identical and you can try to assemble it side by side following steps mentioned below. The AUX PS is the simplest one but also has AC mains section that require additional care when operating. Finally, physically the biggest one – Arduino Shield is modestly populated but also carry extra parts such as TFT touch-screen display, Arduino board, binding posts, etc. that dictate some other set of assembling rules.

A good start could be to check that all parts from the consolidated BOM (https://github.com/eez-open/psu-hw/tree/master/Consolidated/BOM) are available and sorted by type and values and can be easily accessible. As you have probably already learned, simple SMT parts with 2-3 terminals (passives, diode, transistors) can be easily lost even if you have well arranged and clean benchtop. Therefore instead of crying for lost one, simply order few parts more and take another one when previously selected was just gone. That issue is present with both self-locking and regular tweezers.

There is a few methods of storing and sorting SMT parts like small part snapboxes, envelopes etc. Each of them is valuable as far as it can reduce possibility of replacing one part mistakenly with another. That is especially important for ceramic capacitors (MLCCs) that do not carry value marks.

A discipline of selecting a single value at the time (even in larger quantity) and placing them on proper places is of a paramount importance to ensure that PCBs are assembled correctly and will work properly.

When needed tools, bare PCBs and SMT parts are on disposal, one important task still remain before we can start with PCB assembling – it's how to identify part value since PCB's silkscreens (top and bottom) only carry reference designators (i.e. R..., C..., IC..., etc.).

If you are using Eagle then open .brd file and when populating top layer make sure that among other layers 21, 25, and 27 are visible (see Top assembly selected layers.png (https://github.com/eez-open/psu-hw/blob/master/Building%20instructions/Top%20assembly%20selected%20layers.png)). For assembling bottom layer set layers 22, 26, and 28 as visible (see Bottom assembly selected layers.png (https://github.com/eez-open/psu-hw/blob/master/Building%20instructions/Bottom%20assembly%20selected%20layers.png)).

The freeware edition of Eagle also allows you to open .brd file and switch layers on and off.

When installation of the Eagle is not an option, you can use the following images:

- AUX PS r5B9 assembly (top layer).png (https://github.com/eez-open/psu-hw/blob/master/Building%20instructions/AUX%20PS%20r5B9%20assembly%20(top%20layer).png)
- AUX PS r5B9 assembly (bottom layer).png (https://github.com/eez-open/psu-hw/blob/master/Building%20instructions/AUX%20PS%20r5B9%20assembly%20(bottom%20layer).png)
- Arduino shield r3B4 assembly (top layer).png (https://github.com/eez-open/psu-hw/blob/master/Building%20instructions/Arduino%20shield%20r3B4%20assembly%20(top%20layer).png)
- Arduino shield r3B4 assembly (bottom layer).png (https://github.com/eez-open/psu-hw/blob/master/Building%20instructions/Arduino%20shield%20r3B4%20assembly%20(bottom%20layer).png)
- Power board r5B9 assembly (top layer).png (https://github.com/eez-open/psu-hw/blob/master/Building%20instructions/Power%20board%20r5B9%20assembly%20(top%20layer).png)
- Power board r5B9 assembly (bottom layer).png (https://github.com/eez-open/psu-hw/blob/master/Building%20instructions/Power%20board%20r5B9%20assembly%20(bottom%20layer).png)

Above mentioned order of PCBs is not mandatory for assembling process but represents a logical sequence since AUX PS is required for powering Arduino shield and Arduino shield is required for controlling Power boards. Suggested order is also sorted by PCB complexity starting with the simplest one.

If not otherwise specified, we'd like to recommend that parts are soldered in the following order on the same layer:

- Small SMT parts (e.g. passives, diodes, transistors, etc.)
- SMT ICs
- Bulk SMT parts (elco capacitors, power inductors, mosfets and diodes) and
- THT parts (connectors, switches, chokes, etc.)

### Default jumper positions

For various reason on few places on the PCBs a jumpers section are used where zero-ohm resistor is used to define signal path. Some of them define behavior of the circuits (e.g. JP5, JP6, and JP7) and when wired in wrong way or left unpopulated that can create some difficulties and the firmware could not control it properly. To simplify a whole assembly process a clear mark is added next to zero-ohm resistor default position that should insure a proper functionality with current firmware revision. On the picture below above mentioned jumper sections are shown and red rectangle indicate the place for zero-ohm resistor that is in line with “U” shaped mark.

### AUX PS r5B9 assembling

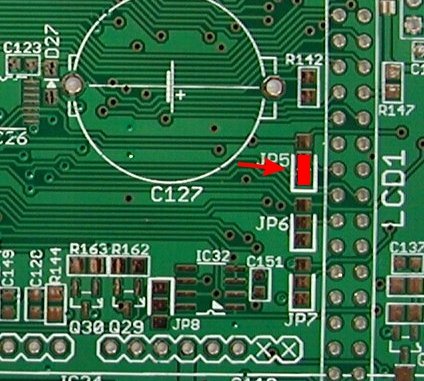
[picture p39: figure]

(http://www.envox.hr/eez/images/jumper_sections.jpg)Fig. 2: Zero-ohm jumpers markings

Schematic for this board is shown on sheets 6/12 (https://raw.githubusercontent.com/eez-open/psu-hw/master/Consolidated/EEZ%20PSU%20consolidated%20r5B9%20Sheet%206of12.png) and 7/12 (https://raw.githubusercontent.com/eez-open/psu-hw/master/Consolidated/EEZ%20PSU%20consolidated%20r5B9%20Sheet%207of12.png). We'd like to recommend the following steps for assembling this board:

- +5 V power supply built around IC16
- Fan control (Q22, X6)
- AC input terminal and protection
- Soft start/stand-by (Q20, Q21, OK1, OK2)
- AC/DC module (TR2) and
- Ethernet and USB terminals (X7, X11)

The IC16 is one of the few parts that require hot air soldering because of exposed power tab placed beneath its plastic body. It has to be mounted in that way to establish a solid electrical and thermal bond with exposed copper on the PCB's top layer. Otherwise, a permanent damage may occur or erratic operation. Due to that this part should be mounted first. When that is done we can proceed with completion of +5 V power supply section. The X5 connector has to be mounted after surrounding SMT parts (D21, R130, R131) otherwise it could be difficult to mount them without damaging X5 by touching it unintentionally with soldering iron body or tip.

When this section is finished and ready for testing do not solder TR2 since it's huge and could make mounting of surrounding parts afterward almost impossible. Instead, use external regulated 12 V supply and connect it properly on its terminal 9- and +7. If everything is soldered correctly, a regulated +5 V will appear on X5 pin 10 (+) and 9 (-).

Now we can proceed with fan control. Keep in mind to mount THT part at the end (X6). Testing of this section has to be postponed until Arduino Shield is assembled. Also, it will require preparation of fan cable which comes without connector.

AC input terminal and protection section contains only THT parts that can be carefully soldered on the bottom layer.

Soft start/stand-by triacs Q20 and Q21 are sharing the same heatsink KK1 mounted on its opposite sides using single screw and nut. They can be mounted on before soldering. Another possibility is to solder heatsink first and then mount on each side a triac and then solder their terminals. Take care that power resistor R107 is of proper type (wirewound) and power rating.

Finally, place TR2 as the latest part on the top PCB layer. Now it's possible to test once again +5 V power supply by carefully applied AC mains on the X4 pin 1, 2 and 5.

On the bottom layer only two parts have to be mounted – Ethernet (X7) and USB (X11) terminals. If you got customized enclosure with pre-drilled holes on its rear panel, we recommend to mount the PCB on the rear panel first (using 14 mm spacers) and then solder that terminals. That will insure that everything fits perfectly.

### Arduino Shield r3B4 assembling

There is no recommended order in which sections on this PCB should be soldered. One possibility is to simply follow the order of sheets in consolidated schematics related to this board (sheet 8/12 (https://raw.githubusercontent.com/eez-open/psu-hw/master/Consolidated/EEZ%20PSU%20consolidated%20r5B9%20Sheet%208of12.png), 9/12 (https://raw.githubusercontent.com/eez-open/psu-hw/master/Consolidated/EEZ%20PSU%20consolidated%20r5B9%20Sheet%209of12.png), 10/12 (https://raw.githubusercontent.com/eez-open/psu-hw/master/Consolidated/EEZ%20PSU%20consolidated%20r5B9%20Sheet%2010of12.png), 11/12 (https://raw.githubusercontent.com/eez-open/psu-hw/master/Consolidated/EEZ%20PSU%20consolidated%20r5B9%20Sheet%2011of12.png), and 12/12 (https://raw.githubusercontent.com/eez-open/psu-hw/master/Consolidated/EEZ%20PSU%20consolidated%20r5B9%20Sheet%2012of12.png)) and to leave the following parts for the end:

- Power relays (K_SER, K_PAR) due to their dimensions
- Super capacitor (C127) for RTC backup
- Push-in connectors (X12, X14) especially if you'd like to follow suggestion to adjust its distance from the front panel as described below
- 40-pin connector (LCD1) for the TFT touch-screen display
- Front panel power switch (SW1)

The revision r3B4 has few issues that we didn't spot before it went into manufacturing but fortunately all of them can be easily fixed.

Red LED polarity

Let's starts with the simplest one which is related to chosen red color LEDs that are located on the PCB's bottom layer. Polarity marking on the PCB is not in line with HSMH-C170 specification. Therefore you simply need to rotate it while soldering.

(http://www.envox.hr/eez/images/red_led_marking.jpg)Fig. 3: Red LEDs incorrect markings on the Arduino Shield bottom layer

Output capacitors mounting

We are using SMT EEEFK1J220P (22 μF) as output capacitors (C106, C111) that are wider in diameter than THT UPW1J150MED (15 μF) initially specified. The SMT pads provided on that positions are also for SMT capacitors smaller in diameters. Regardless of that, mentioned type can be easily mounted by simply bending its terminals when it becomes a THT. Now, holes for a THT part can be used for soldering.

Additional output capacitors

An additional capacitor is recommended on the power output. A ceramic 1 μF, 50 V capacitor is used and damped with 1 Ω resistor. They should be placed as close as possible to the output binding post holes but there is no predicted place for that on this PCB revision. Nevertheless it's simple to add them as it is shown on Fig. 4.

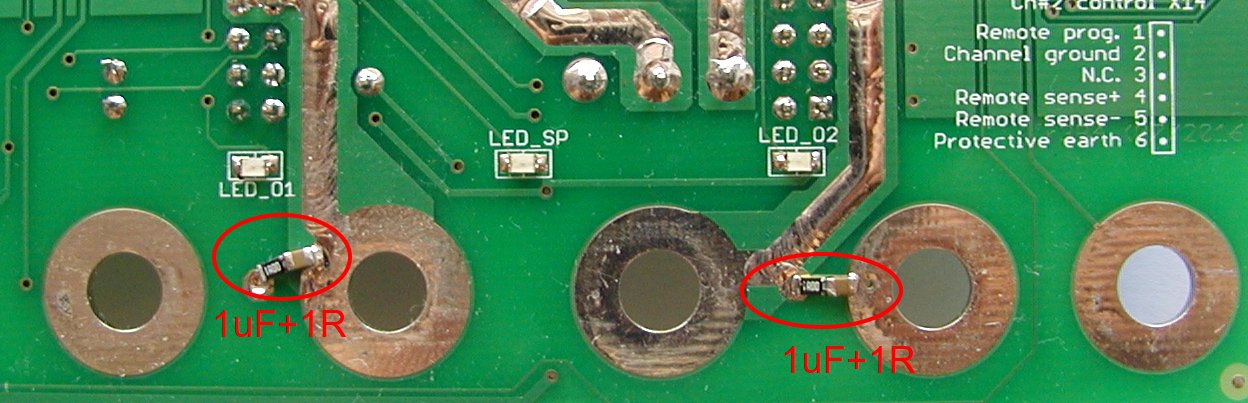
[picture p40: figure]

(http://www.envox.hr/eez/images/additional_capacitors.jpg)Fig. 4: Additional channel's output RC circuit

Ethernet connector position

The Ethernet connector (X18) is not properly positioned – it is too close to the CH1's heatsink. Due to that it is not possible to insert Ethernet cable that connect output terminal on the rear panel (via X8 on the AUX PS board).

A right angle connector has to be used as specified in the BOM. But, when such connector type is used (see Fig. 5), there is no possibility to put a screw to fix TFT touch-screen display on the lower left corner viewed from the display's back (or lower right corner viewed from the display's front).

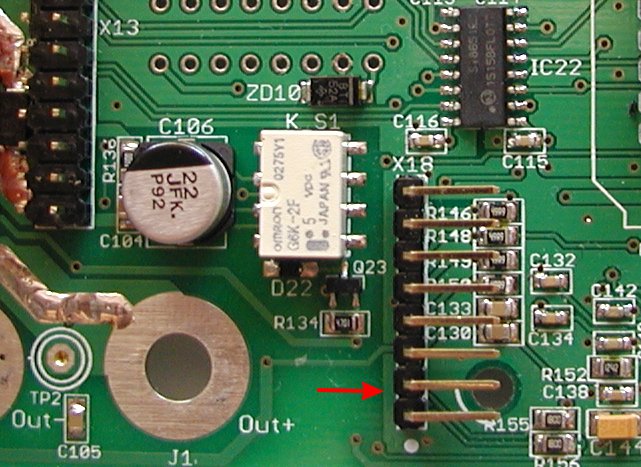
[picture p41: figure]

(http://www.envox.hr/eez/images/ethernet_connector.jpg)Fig. 5: Ethernet header on the Arduino shield

Fortunately that is not a big issue since display still can be fixed on all four corners with 11 mm spacers and that will provide enough mechanical strength required to withstand finger pressure on that part of the display (Fig. 6).

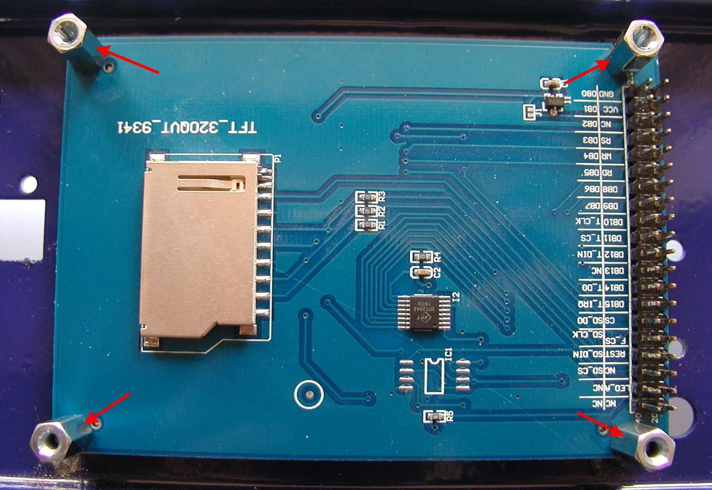
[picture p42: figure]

(http://www.envox.hr/eez/images/tft_display_spacers.jpg)Fig. 6: TFT touchscreen display rear view

Push-in connectors distance adjustments

Distance between rear side of the front panel and the Arduino Shield PCB is defined by TFT display that is approx. 18 mm:

- 5 mm display thickness
- 1.5 mm display PCB thickness
- 11 mm spacer between display and plastic washer (defined by LCD1 connector height) and

Height of the push-in connectors (X12, X14) is 14 mm and when they are soldered directly on the PCB they will be 4 mm apart from the front panel surface. That does not mean that their pins are not accessible. It's more a question of visual appearance and you can fix that with modified cheap DIL16 sockets. You need to cut them horizontally and insert each half separately since distance between push-in connector's rows is different. You also need to adjust their height to 4 mm (usually that is about 5 mm). That can be done in a matter of minute using a piece of sandpaper.

Insert push-in connectors into modified sockets before soldering. To improve mechanical strength you can also apply e.g. hot glue (https://en.wikipedia.org/wiki/Hot-melt_adhesive).

(http://www.envox.hr/eez/images/push-in-with-spacers.jpg)Fig. 7: Push-in connectors with extensions

Keep in mind that X12 and X14 have to be mounted on the bottom side of the PCB:

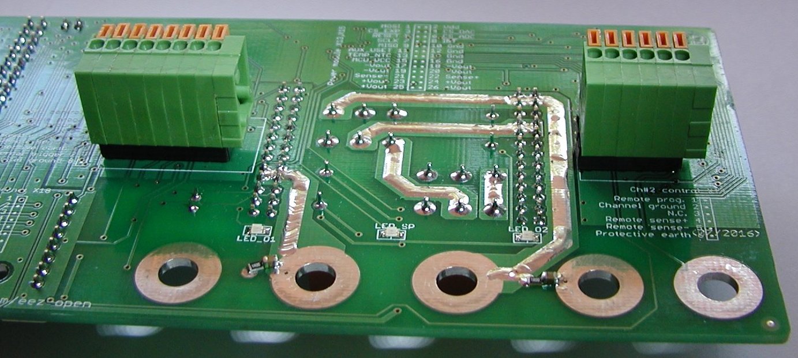
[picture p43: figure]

(http://www.envox.hr/eez/images/push-in-with-spacers-mounted.jpg)Fig. 8: Push-in connectors mounted on the Arduino shield

The end result looks like this:

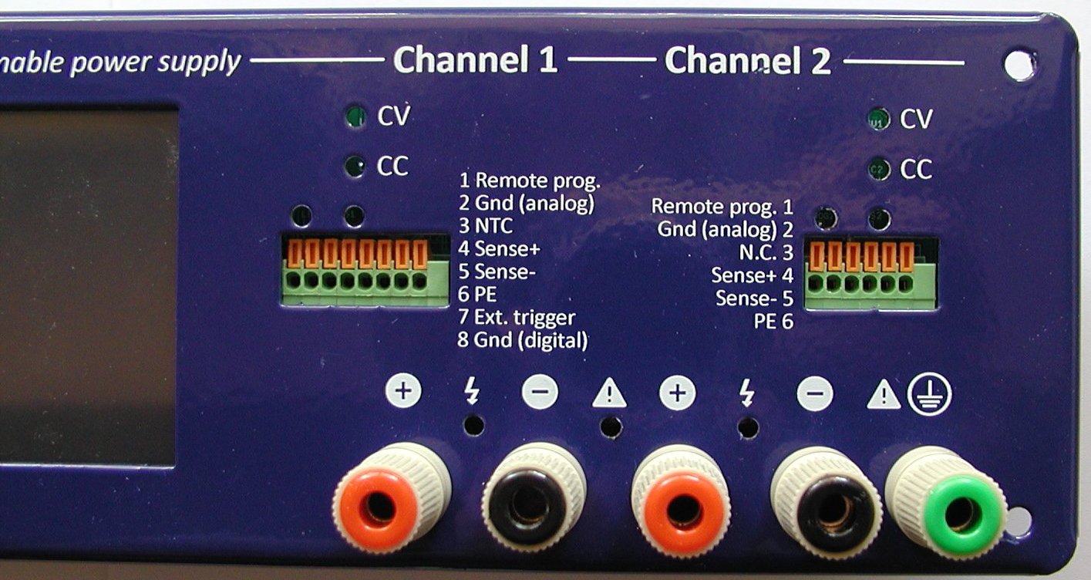
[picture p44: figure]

(http://www.envox.hr/eez/images/push-in-with-spacers-front.jpg)Fig. 9: Front panel with push-in connectors mounted

When all SMT parts are mounted, followed by THT parts, we can solder few parts mentioned on the beginning:

- The power relay now should not interfere with mounting of any surrounding parts.
- The super capacitor is polarized as elco capacitors or battery cell. Check its terminals polarity twice before mounting!
- If push-in connectors X12 and X14 is not inserted into sockets, as it's suggested above, then we can now proceed with their soldering on the bottom side of the PCB.
- TFT touch-screen display connector (LCD1) has to be soldered on the bottom side too. If we want to be completely sure that it's aligned with display, we can mount display on the customized enclosure first, then insert 40-pin connector on display's header, and finally place the PCB on top of display. Use plastic washer between 11 mm spacers and PCB and another one between PCB and M3 mounting screw. We have to check alignment of the PCB with output binding posts holes and when everything is in place 40-pin connector can be soldered.
- Finally, we can mount power switch. Once again, it's recommended to see how it's aligned with the corresponding hole on the enclosure's front panel first, then adjust its position and start with soldering.

When all parts are mounted and PCB is properly cleaned, an Arduino Due board can be installed. It has to be loaded with appropriate firmware (M2 (https://github.com/eez-open/psu-firmware/releases/tag/m2) or newer) that is configured to work with this board revision. Use its USB named Programming port for firmware upload.

If everything is assembled correctly and firmware is successfully uploaded, the welcome screen should appear after reset or new power on. The firmware will proceed with self-test and check peripherals and channels as defined in conf.h, or override with parameters in the user_conf.h file.

The AUX PS module r5B9 has mistakenly connected pin 1 of the USB header to the USB cable. Therefore even if the PSU is completely switched off, the Arduino shield will be powered from the external source if USB cable is connected. The easiest way to fix that issue is to detach pin 1 (red) wire and insulated it as shown on the Fig. 10.

### Power board r5B9 assembling

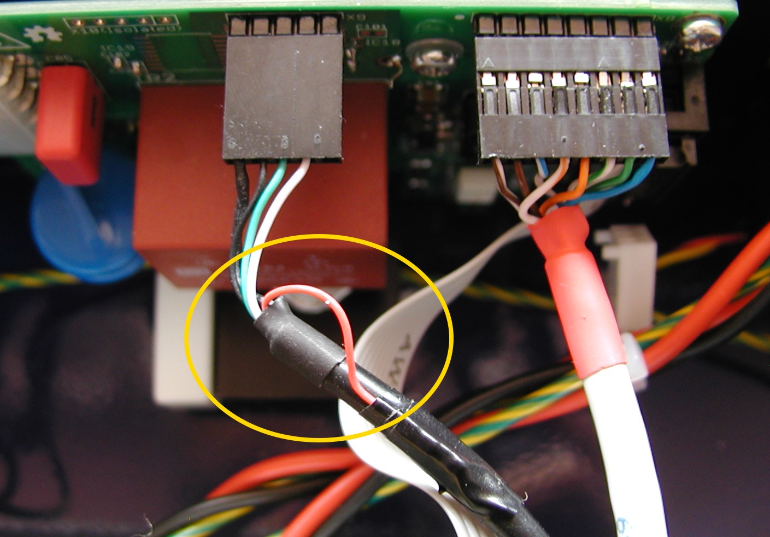
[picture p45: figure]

(http://www.envox.hr/eez/images/usb_cable_hack.jpg)Fig. 10: USB cable hack

According to the number of components and functionality, the Power board is the most complex part of this PSU. We'd like to recommend assembling of this board in the following steps:

- Power pre-regulator
- Bias power supply
- Post-regulator

After each section is completed, perform simple testing described below before continuing with the assembling.

Power pre-regulator

The power pre-regulator circuit is shown on Sheet 1/12 (https://raw.githubusercontent.com/eez-open/psu-hw/master/Consolidated/EEZ%20PSU%20consolidated%20r5B9%20Sheet%201of12.png). We recommend you to start with IC1 that, as in case of IC14, require soldering of exposed thermal pad. A hot air soldering station instead of soldering iron should be used here. This section also require soldering on the PCB’s bottom side (L1 and X1). That should not be a problem if you are using PCB holder. If you choose to supply Power board with AC instead of DC input, follow Hack #1 (http://www.envox.hr/eez/bench-power-supply/hacking-area.html#hack1).

Once again, keep in mind to mount all smaller parts first and than continue with bulky one such as L2, C18, C16, etc.

When everything is in place, you can proceed with basic testing. Since the board is not fully assembled, it cannot be done without some tricks. The first possible obstacle to check if pre-regulator works properly is existence of Q3 that is used to enter 100% duty cycle when the pre-regulator is bypassed. The IC1 is then effectively switched off and instead of switching frequency a DC signal will be present on Q1 gate (hence the name 100% duty cycle). But, we’d like to test in this step if switching works or not. We have two possibilities here:

- To apply +5 V (use some external source in this stage) to Q3 gate by soldering a thin wire e.g. used for wire wrap (https://en.wikipedia.org/wiki/Wire_wrap) to that position or locate pin 13 on IC9 (see Sheet 4/12 (https://raw.githubusercontent.com/eez-open/psu-hw/master/Consolidated/EEZ%20PSU%20consolidated%20r5B9%20Sheet%204of12.png)) and do the same or
- simply place zero-ohm resistor on position R13. Note: don’t forget to remove it before start testing the Post-regulator section and IC9 is mounted.

Before we can apply input power we need to provide some signal on trace OUT+. The easiest way is to locate any of pins 23 to 26 on X3 connector. Do not solder X3 connector in this stage because you’ll have difficulty with mounting surrounding parts like e.g. R95, R105, C84, Q19, etc.

Again, an external regulated source is needed. We can use the same +5 V used to turn on Q3 or something else with output of up to +40 V. In fact, we can start testing by simply connecting OUT+ to the ground. If OUT+ is grounded we can check with the scope two points to see if pre-regulator works:

First is “hot-spot” (SW, magenta trace) where Q3 drain, power inductor L2 and D5 cathode are connected. Use x10 probe. There is also a place for additional R4 and PCB test point (example (http://export.farnell.com/harwin/s1751-46r/test-terminal-pcb-smt/dp/2293786)) on the PCB where you can hook probe securely. Another test point is PREG_OUT (Preg, cyan trace), output from the power pre-regulator.

Fig. 11 shows measurement when +OUT is set to 0 V (grounded). Its output voltage will vary depending on connected load and difference between post-regulator output, and power pre-regulator output. Mentioned voltage difference could be about +6.5 V for no load to less then +3 V for full load of 5 A. Fig. 12 is another example without load when +5 V is used for pre-regulator’s output voltage programming (measured PREG_OUT is +10.8 V).

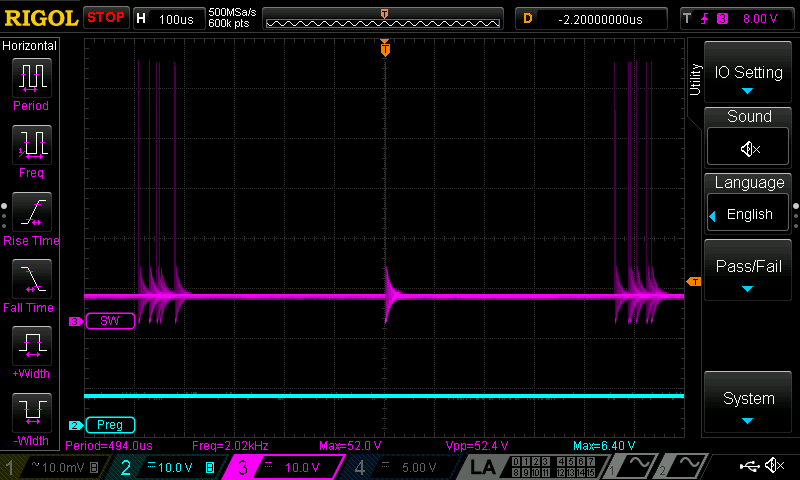
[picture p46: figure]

(http://www.envox.hr/eez/images/pre-regulator-test-0v-noload.png)Fig. 11: Pre-regulator measurements, +VOUT = 0 V (grounded, no load)

(http://www.envox.hr/eez/images/pre-regulator-test-5v-noload.png)Fig. 12: Pre-regulator measurements, +VOUT = 5 V, no load is connected

Please note that in both cases the SW signal looks erratic but that is only because no load is connected. On Fig. 13 is shown characteristic switching pattern when load is connected (e.g. power resistor of 10 Ω).

Finally on Fig. 14 is shown what will happen if Q3 is not turned on. The IC1 will enter 100% duty cycle because chosen values for voltage divider in feedback loop (R12, R15) are set well over pre-regulator input voltage to 56 V while input voltage is not higher then 50 V.

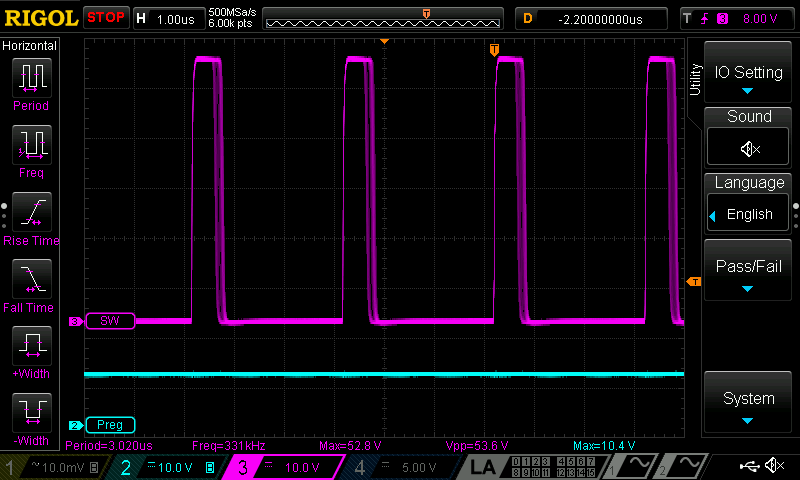
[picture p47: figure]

(http://www.envox.hr/eez/images/pre-regulator-test-5v-load_8r2.png)Fig. 13: Pre-regulator measurements, +VOUT = 5 V with load connected

If you’d like to test this scenario be sure that no load is connected, otherwise a Q1 SOA could be easily exceeded that can damage Q1 permanently (with unknown consequences for IC1 too).

The so-called Low noise mode of operation when pre-regulator works with 100% duty cycle will remove from channel’s output hard to filter switching noise. But working in that mode puts real limitation in output power and if the PSU will be used for application where higher output ripple can be easily tolerated it’s possible to disable that option by removing Q3 and mount permanently zero-ohm resistor on position R13.

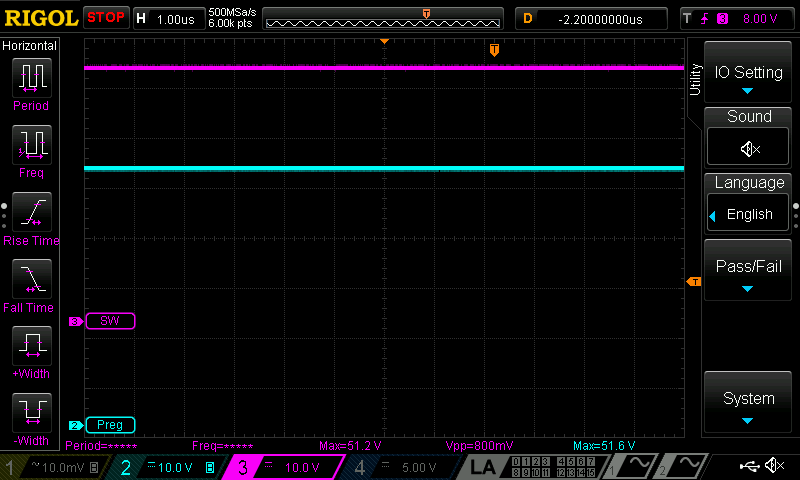
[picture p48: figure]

(http://www.envox.hr/eez/images/pre-regulator-low-noise-noload.png)Fig. 14: Pre-regulator in 100% duty cycle, without load connected

Bias power supply (switching pre-regulator and LDOs)

The sheet 2/12 (https://raw.githubusercontent.com/eez-open/psu-hw/master/Consolidated/EEZ%20PSU%20consolidated%20r5B9%20Sheet%202of12.png) has to be followed for bias power supply circuit assembling. It does not require any special instructions and when everything is in place we can proceed with basic testing. Please note that power pre-regulator will be now also powered and make sure that no load remains connected on the PREG_OUT from the previous testing. Obviously, the first thing that we can test are output voltages on points +V (IC2), -V (IC3) and +5V (IC5). They should to be within 5 % tolerance +5 V, -5 V and +5 V.

Another two points of interest are SW (IC4) and PWRGOOD (IC5). The good place for probing SW signal is pin 1 on TR1 or D10 cathode. Fig 15 shows typical waveform on that point:

It’s interesting to see how the PWRGOOD relates to change of input voltage. That signal will be actively monitored with MCU and it will push the PSU into Stand-by mode as soon as possible when its changed from high to low level. Fig. 16 and Fig. 17 shows transition while input power is applied and removed.

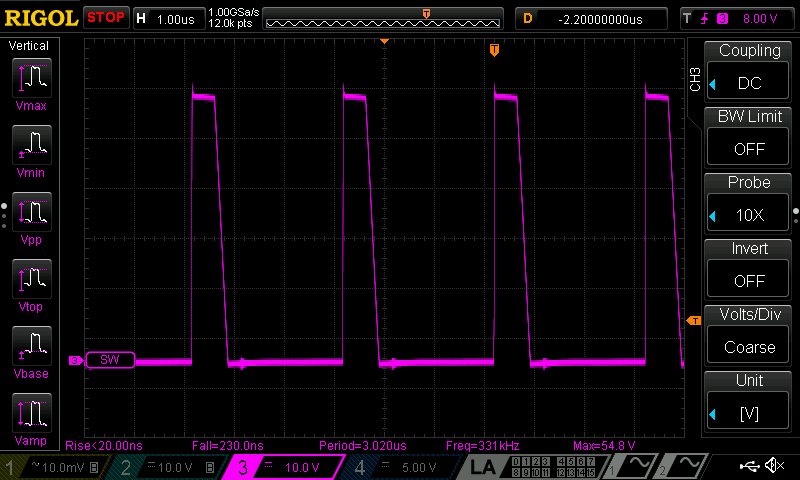
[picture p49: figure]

(http://www.envox.hr/eez/images/bias-pre-regulator-sw.png)Fig. 15: Bias pre-regulator SW output

(http://www.envox.hr/eez/images/powergood_power_on.png)Fig. 16: PWRGOOD signal transition (Power on)

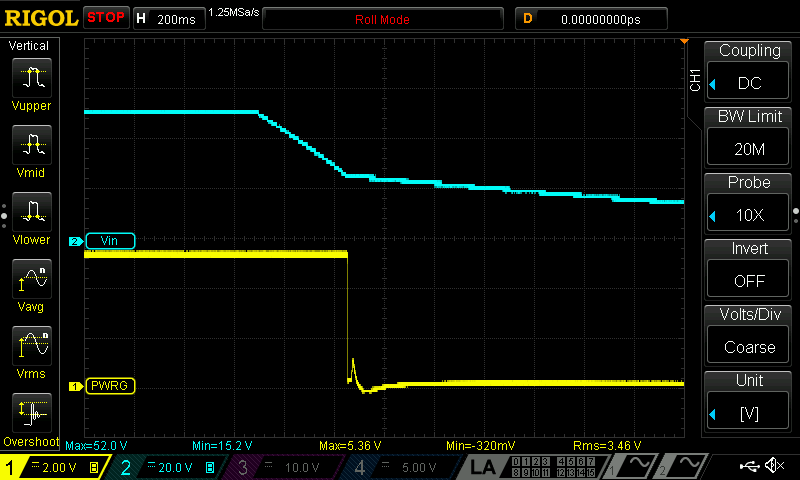
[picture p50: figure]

(http://www.envox.hr/eez/images/powergood_power_off.png)Fig. 17: PWRGOOD signal transition (Power off)

Post-regulator

The post-regulator circuits can be found on Sheets 3/12 (https://raw.githubusercontent.com/eez-open/psu-hw/master/Consolidated/EEZ%20PSU%20consolidated%20r5B9%20Sheet%203of12.png), 4/12 (https://raw.githubusercontent.com/eez-open/psu-hw/master/Consolidated/EEZ%20PSU%20consolidated%20r5B9%20Sheet%204of12.png) and 5/12 (https://raw.githubusercontent.com/eez-open/psu-hw/master/Consolidated/EEZ%20PSU%20consolidated%20r5B9%20Sheet%205of12.png). The power mosfet (Q4) require special attention. It’s THT part and before soldering we have to bend its terminals as is shown on Fig. 18.

The Q4 has to be mounted on PCB’s bottom layer, and if EEZ H24005 customized enclosure is used, please ensure that distance between its surface area and PCB bottom side is 5 mm. The easiest way to accomplish that is to mount PCB on the heatsink (Fig. 19) using spacers, then mount Q4 (do not forget insulation!), fix it with M3 screw and then start with its soldering.

(http://www.envox.hr/eez/images/q4_bending.jpg)Fig. 18: Q4 preparation for mounting

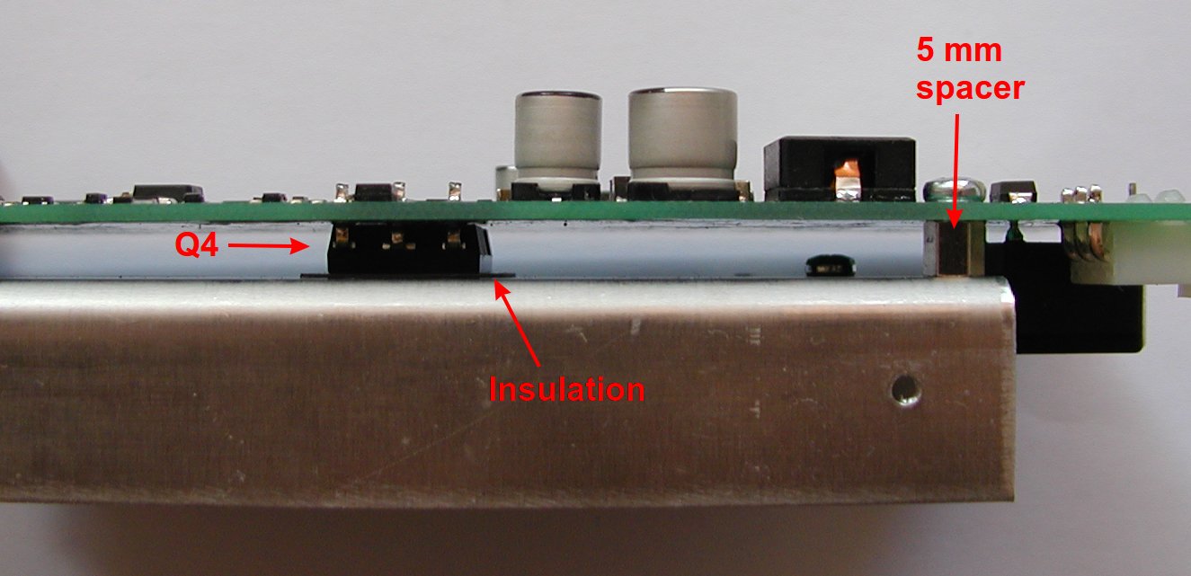
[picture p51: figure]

(http://www.envox.hr/eez/images/q4_mounting.jpg)Fig. 19: PCB side view with Q4 mounted on heatsink

It is highly recommended that below power pre-regulator section a piece of 5 mm thick silicone thermal pad is mounted (search e.g. AliExpress (https://www.aliexpress.com/wholesale?SearchText=100mm+5mm+thermal+pad)). Channel temperature that is measured with NTC1 can be lowered in that way significantly. With e.g. 20 mm wide pad (Fig. 20) it’s possible to achieve 6 oC temperature drop on the max. load. Lowering temperature will also affect cooling fan operation which will work with lower speed and makes it quieter.

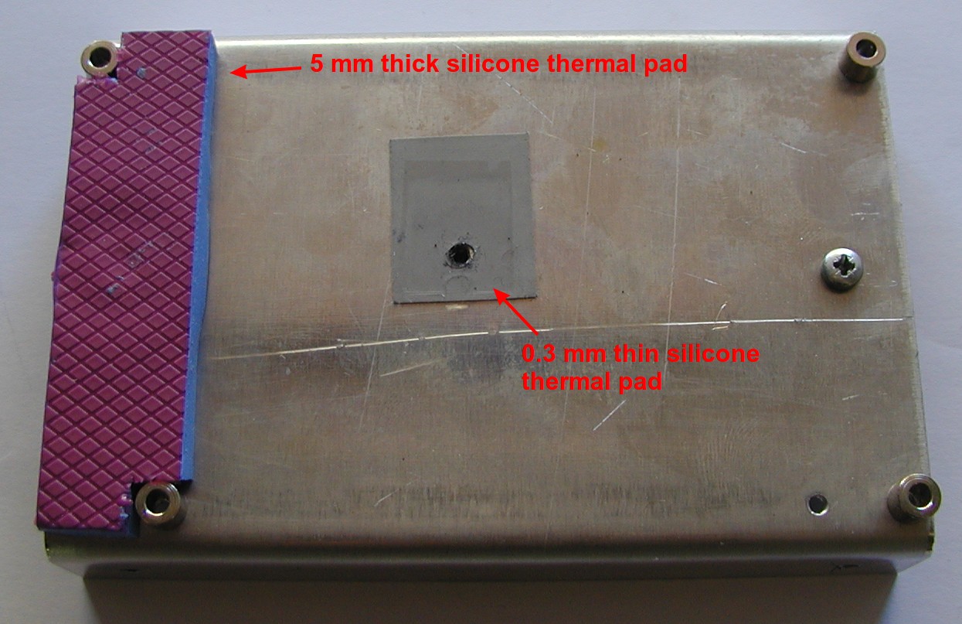
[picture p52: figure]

(http://www.envox.hr/eez/images/silicone_pads.jpg)Fig. 20: Silicone thermal pads

Do not use conductive thermal pad (e.g. aluminium block with PCB side insulated) since it will drastically increase switching noise!

When everything is mounted, you can check few points before connecting it with the Arduino Shield that is required for controlling the Power board:

Signal | Value | location | Comment
+VREF | +2.5 V | IC10 | Define overall precision
+OUT | around zero | Pin 23-26, X3
CV_ACTIVE | +5.1 V (logical high) | R88/R92 | CV mode active (if U_SERVO is negative)
CC_ACTIVE | +0.6 V (logical low) | R101/R104
POST_OE | +4.67 V (logical high) | R56 | Output is disabled
U_SERVO | -1.1 V | D15 cathode
I_SERVO | +0.28 V | D17 cathode

Corrections

During the assembly and testing two issues are found on this board that will require PCB modifications. Fortunately both can be done without considerable effort or special skills. The simpler one is related to radiated EMI. One of the PCB’s mounting holes is wired to the protective earth potential and the mounted heatsink for the Q4 become also on that potential when it’s fixed on the PCB. Our intention was to attenuate EMI in that way, but the end results is quite contrary when the Power board is mounted into metal (conductive) enclosure! It seems that in that way a whole enclosure is earthed not on one but on three different point (one close to the AC inlet and two via above mentioned wiring of the heatsink) and that generate ground loops.

If you are going to use metal enclosure, it is advisable to simply cut the earth trace that leads to the mounting hole which is near L2 power inductor as shown on Fig. 21. Use miniature drill with a diamond mill (example (http://www.tme.eu/en/details/d-1712/power-tools-parts-and-accessories/donau/)) for that.

Another issue is connected with selection of the voltage programming source that in our case can be internal (DAC output, IC11) or external signal input (+2.5 V full scale) available via miniature push-in connectors located on the Arduino Shield (X12, X14). Due to the mistake on PCB layout only internal programming (that is default) is possible. To overcome this issue we need to cut U_SET_OUT trace that goes to R52 and connect it to R81 (Fig. 22).

(http://www.envox.hr/eez/images/heatsink_earth.jpg)Fig. 21: Earth PCB trace cut

A thin wire (e. g. for wire wrap) about 5 mm long is needed to be soldered (Fig. 23, pos. A) and PCB trace has to be cut (Fig. 23, pos. B).

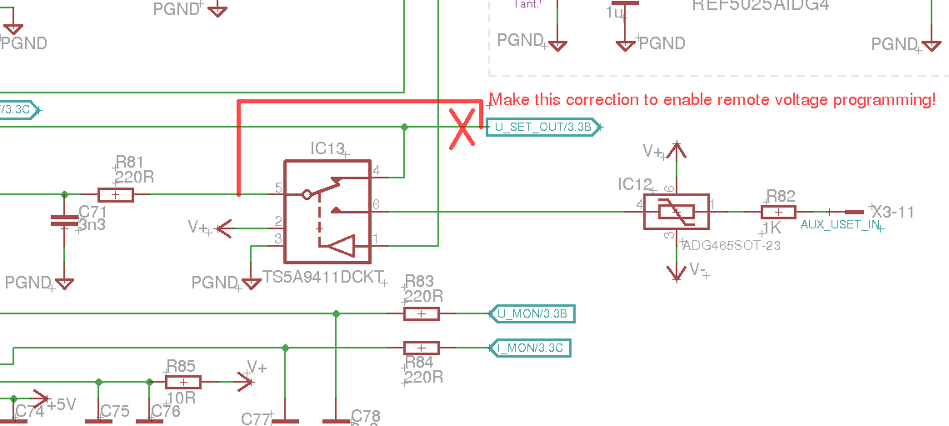
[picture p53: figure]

(http://www.envox.hr/eez/images/rprog_correction_sch.png)Fig. 22: Voltage programming selection schematic modification

## Firmware uploading

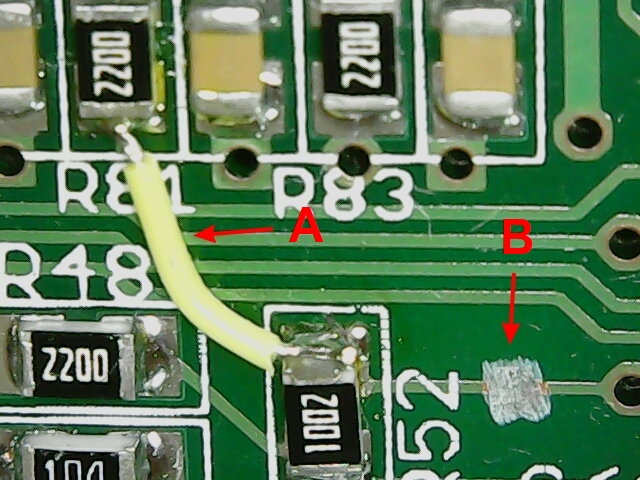
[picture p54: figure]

(http://www.envox.hr/eez/images/rprog_correction2.jpg)Fig. 23: Voltage programming PCB modification

The PSU firmware is an Arduino sketch. Therefore for its compilation and uploading to the Ardunino Due board that resides on the Arduino Shield you have to install and run cross-platform Arduino IDE which can be downloaded here (https://www.arduino.cc/en/Main/Software).

Installing Arduino IDE is not enough in our case because support for ARM boards such as Due is not installed by default. Therefore you have to add ARM Cortex-M3 board support. Navigate to Tools… Board:… Boards manager and select for installation Arduino SAM Boards package. When it’s successfully installed, you can check that as shown in the Fig. 24.

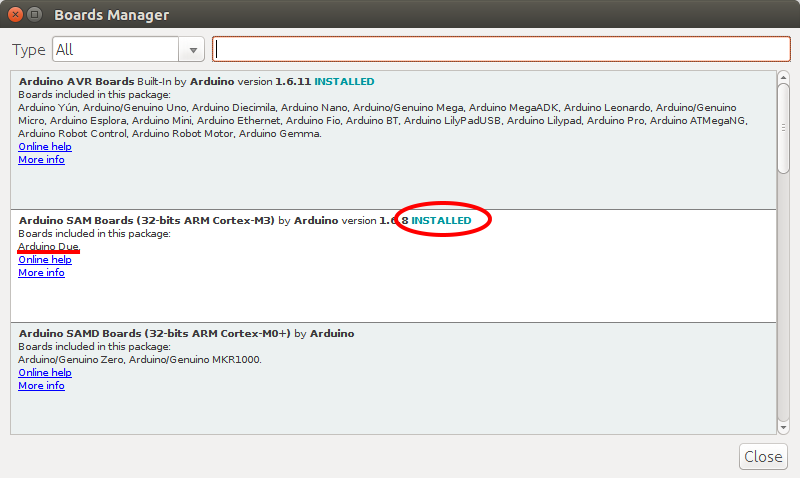
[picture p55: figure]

(http://www.envox.hr/eez/images/arduino_boards_manager.png)Fig. 24: Arduino boards manager with installed support for Due

Next step is selection of Board and USB since Arduino Due board has two USB ports. We’ll use Programming Port as shown on Fig. 25.

The Arduino IDE is now ready for work and we can continue with downloading firmware from the GitHub repository. The Arduino Shield r3B4 or newer require firmware revision M2 that can be found in Master (https://github.com/eez-open/psu-firmware/tree/master) branch.

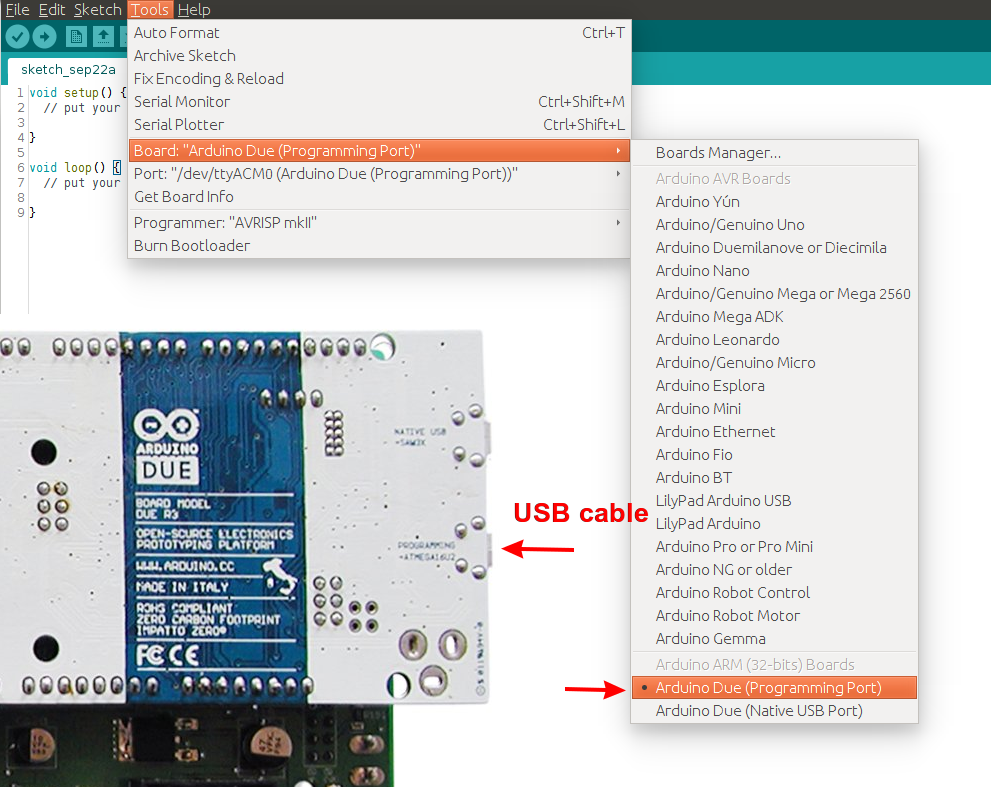
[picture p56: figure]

(http://www.envox.hr/eez/images/due_usb_port_selection.png)Fig. 25: Arduino DUE USB port selection

Move to Clone or download option and select Download ZIP option to save the latest build on your PC (Fig. 26).

When downloaded master.zip package is extracted, the following folder’s tree should be created:

(http://www.envox.hr/eez/images/firmware_download_m2.png)Fig. 26: Firmware download

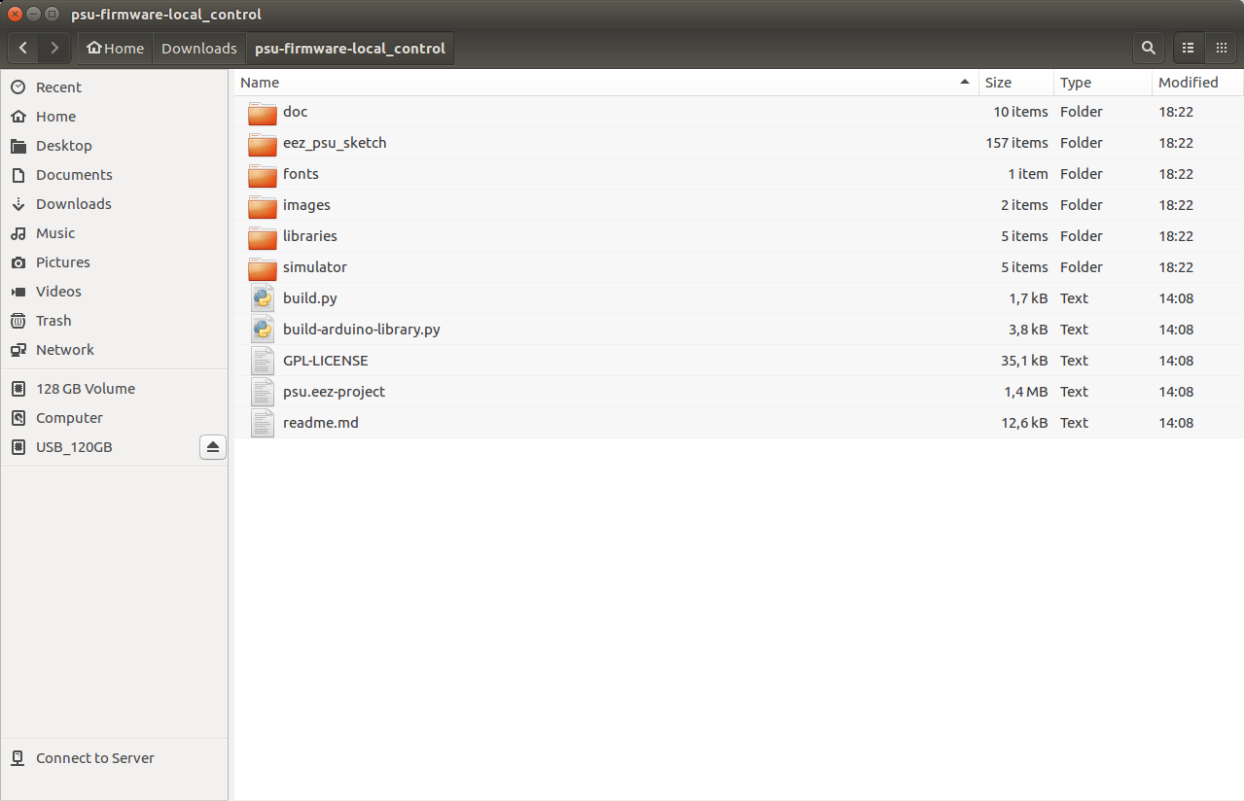
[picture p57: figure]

(http://www.envox.hr/eez/images/firmware_folders.png)Fig. 27: Firmware folders (Ubuntu Linux)

Contents of two folders will be used for firmware compiling within the Arduino IDE: eez_psu_sketch and libraries. The contents of former one has to be copied into Arduino folder that contain 3rd party libraries. That could be e.g. /home/denis/Arduino/libraries on Linux or My Documents\Arduino\libraries on Windows.

The firmware upload require the following steps:

- Power Arduino Shield board
- (Re)start Arduino IDE
- Check if proper USB port is selected under Tools… Port:
- Load firmware sketch eez_psu_sketch.ino (File… Open)
- Start Upload (Sketch… Upload or select the Upload icon on toolbar)
- When the upload process will ends up with an error as shown on Fig. 28 press the RESET button on Arduino Shield board or Arduino Due

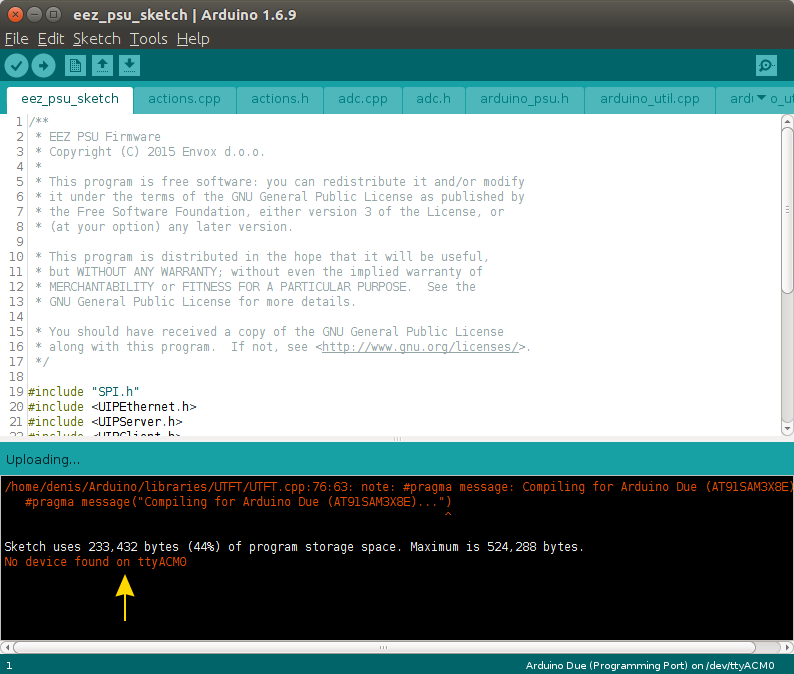
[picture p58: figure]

- Start the upload procedure once again. If Arduino board is successfully reset upload progress bar will appear after compiling (Fig. 29). (http://www.envox.hr/eez/images/fw_upload_err.png)Fig. 28: Arduino sketch (firmware) upload error

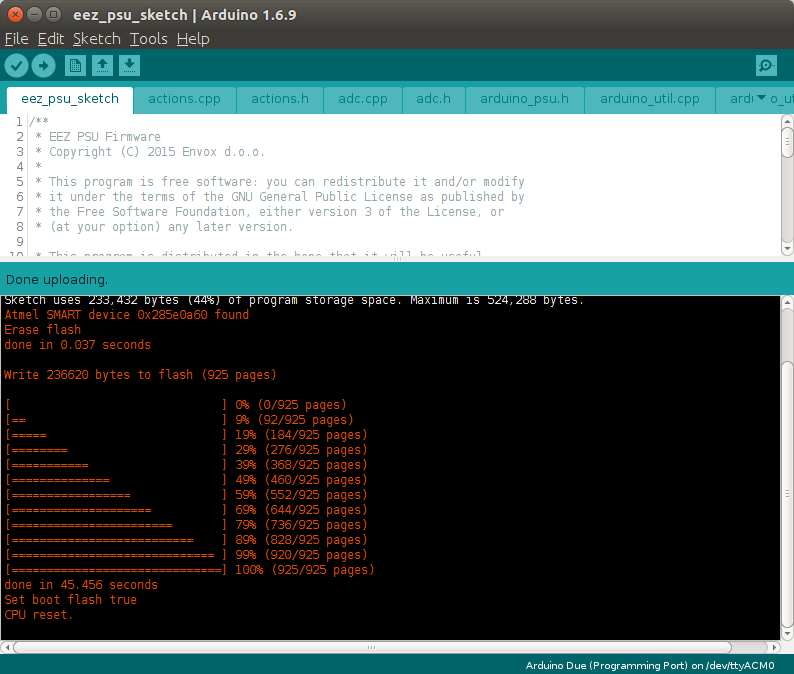
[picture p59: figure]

- You have to reset Arduino once again regardless of the message “CPU reset” that will appear at the end of the uploading process. (http://www.envox.hr/eez/images/fw_uploaded.png)Fig. 29: Arduino sketch is successfully uploaded

On first start the initial touchscreen calibration page (Fig. 30) will be displayed otherwise a welcome page (Fig. 31) will be displayed for few seconds. You cannot skip this test since without calibrated touchscreen interaction could be erratic or even impossible.

(http://www.envox.hr/eez/images/tft_init_calib.png)Fig. 30: Initial screen calibration on first power on

When initial touchscreen calibration is finished, the self-test will be initiated and it is a good indicator that all control over all circuits can be established. If self-test is passed, no additional message will be displayed, and firmware will proceed with the main page (Fig. 32).

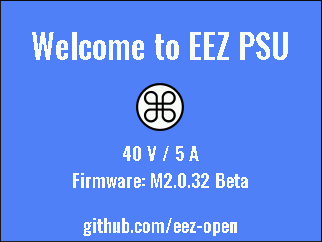
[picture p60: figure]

(http://www.envox.hr/eez/images/tft_welcome_page.png)Fig. 31: Welcome page

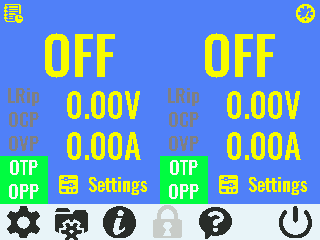
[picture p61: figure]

(http://www.envox.hr/eez/images/tft_main_page2.png)Fig. 32: Main page

Work in progress

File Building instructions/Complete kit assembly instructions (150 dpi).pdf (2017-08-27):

## EEZ H24005 group buy kit assembly instructions

A work in progress (Draft 0.9)

Introduction

Instructions presented in this document are related to Complete kit for EEZ H24005 power supply offered through crowdfunding campaign. (https://www.crowdsupply.com/envox/eez-h24005/crowdfunding) If you intended to build one from the scratch e.g. having only bare PCBs to start with, please refer to EEZ PSU H24005 building instructions (r5B12). (http://www.envox.hr/eez/bench-power-supply/building-instructions.html)

The EEZ H24005 (PSU) kit is not an end user product. As such it was not put into any conformance testing and it may not comply with some or any technical or legal requirement that are applicable to finished products including, without limitation, directives regarding electromagnetic compatibility, recycling (WEEE), FCC, CE, or UL. Assembling and using the PSU requires an understanding of electronic circuits and basic computer programming skills.

If you need assistance, please contact us using this form (http://envox.hr/eez/contact-us.html) or post your problem on the EEVblog forum here. (http://www.eevblog.com/forum/projects/diy-programmable-dual-channel-bench-psu-0-50v3a/) Or, feel free to open a New issue on GitHub here, (https://github.com/eez-open/psu-hw/issues) but please check first to see whether a similar issue already exists).

Only tool required for kit mechanical assembly is medium Phillips head screwdriver. Of course, a multimeter for checking wiring and voltage on few points during the assembly is recommended.

Before you start

We made our best effort to make your EEZ H24005 kit complete and functional. But, please note that due to limited resources kit is not completely and thoroughly tested. Basic testing were performed on the following parts:

- Core modules (i.e. Aux power module, (http://www.envox.hr/eez/bench-power-supply/psu-auxiliary-supply.html) Power boards (http://www.envox.hr/eez/bench-power-supply/power-board.html) and Arduino (http://www.envox.hr/eez/bench-power-supply/psu-digital-control.html) Shield) (http://www.envox.hr/eez/bench-power-supply/psu-digital-control.html)
- Arduino Due (plugged into Arduino Shield)
- 3.2” TFT touchscreen display (plugged into Arduino Shield)

Core modules are tested on our “testbed” but not with using wire harness and AC/DC modules that comes with your kit. Therefore it’s highly recommended that you check visually, mechanically and with ohmmeter if cables are properly assembled before you proceed with final assembling (consult Wire harness (http://www.envox.hr/eez/bench-power-supply/wire-harness.html) section). Please also check Troubleshooting section at the end of this document.
Basic testing covered communication over Ethernet, fan control, power control, touchscreen functionality, beeper, TFT display and output voltage and current programming in a whole range (i.e. up to 40 V and 5 A with connected load and not calibrated!).
AC/DC modules are capable of working with both 115 and 230 Vac. Few of them are randomly selected and tested on 230 Vac. Therefore it would be a wise step to test them before they’re wired with the rest of the unit.
Please note that they comes in cardboard box with voltage stamped on (see Fig. 1, item 5), but that voltage denote fuse ratings only (i.e. 4 A for 230 Vac or 8 A for 115 Vac). If you are going to use it with 115 Vac you have to change switch position as described in section AC/DC modules.

Kit assembly steps

1. Package content
2. Plastic bags content
3. Bottom plate
4. Rear panel
5. AC/DC modules
6. Front panel
7. Power boards
8. Final steps
9. Powering up, calibration and firmware upload
10. Troubleshooting
Revision: 0.9 | 1 (of 22) | Last modified: 2017-08-27

DRAFT – Group buy kit assembly instructions

Package content
The PSU complete kit consists of the following parts, as shown in Fig. 1:
1. Top and bottom plates
2. Front panel box
3. Rear panel box
4. Plastic bags with wire harness and miscellaneous mounting parts
5. AC/DC modules box
6. Power boards box
7. Extra parts (for EEZ H24005 enclosure kit only!)

Please note that AC power cord is not included into this kit.

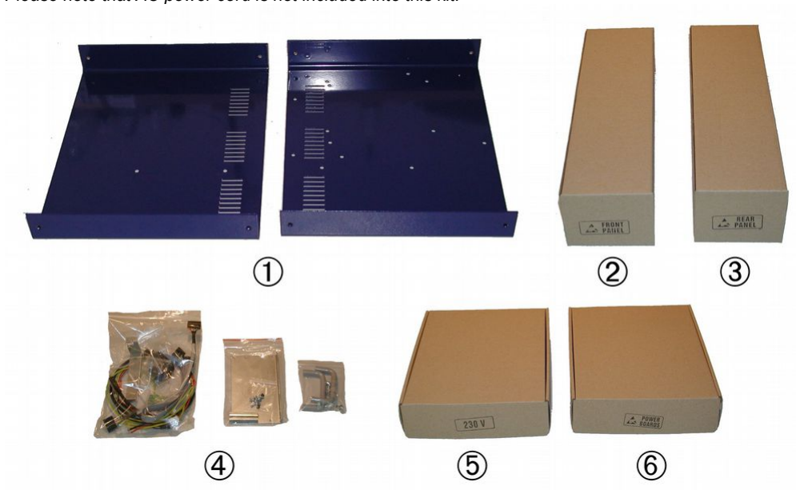
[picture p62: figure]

Rear panel box contains enclosure’s rear panel with mounted AUX power module, (http://www.envox.hr/eez/bench-power-supply/psu-auxiliary-supply.html) IEC AC inlet, 60 mm cooling fan with finger guard and Cable Set #2. (http://www.envox.hr/eez/bench-power-supply/wire-harness.html#cable_set2)

Plastic bags content
Before start assembling please take some time to check if content of plastic bags includes all what is listed below. Also familiarize with Position naming that will be used in the rest of the document.
Last modified: 2017-08-27 | 2 (of 22) | Doc. version: 0.9

Fig. 1: EEZ H24005 Complete kit box content

DRAFT – Complete kit assembly instructions

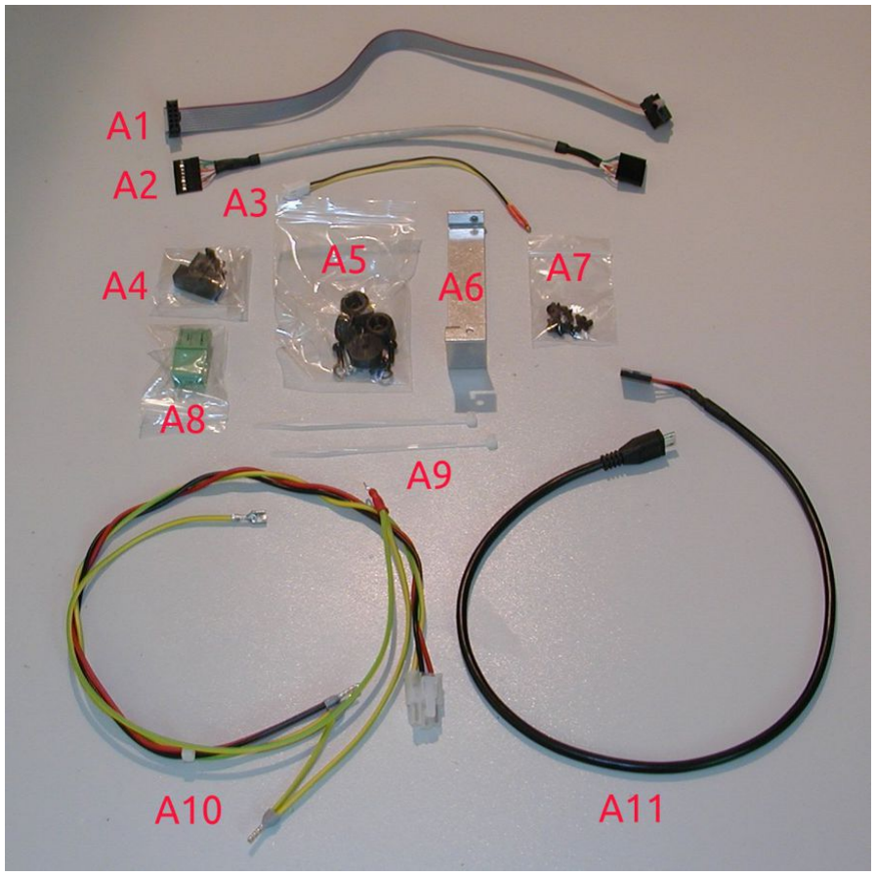
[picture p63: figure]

Position | Description
A1 | 10-pin IDC cable (AUX power module – Arduino Shield)
A2 | Ethernet patch cable (AUX power module – Arduino Shield)
A3 | AUX temperature sensor (Arduino Shield)
A4 | Fuse drawer (IEC AC inlet)
A5 | Enclosure feet pack
A6 | AC&DC module connector cover
A7 | M3 x 5 mm bolts for enclosure (11 pcs)
A8 | DOUT2 plug-in connector (AUX power module)
A9 | Polyamide cable ties (2 pcs)
A10 | Cable set #1 (http://www.envox.hr/eez/bench-power-supply/wire-harness.html#cable_set1)
A11 | Micro USB to 5-pin 0.1” header cable (AUX power module – Arduino Shield)
Revision: 0.9 | 3 (of 22) | Last modified: 2017-08-27

Fig. 2: Plastic bag #1 content

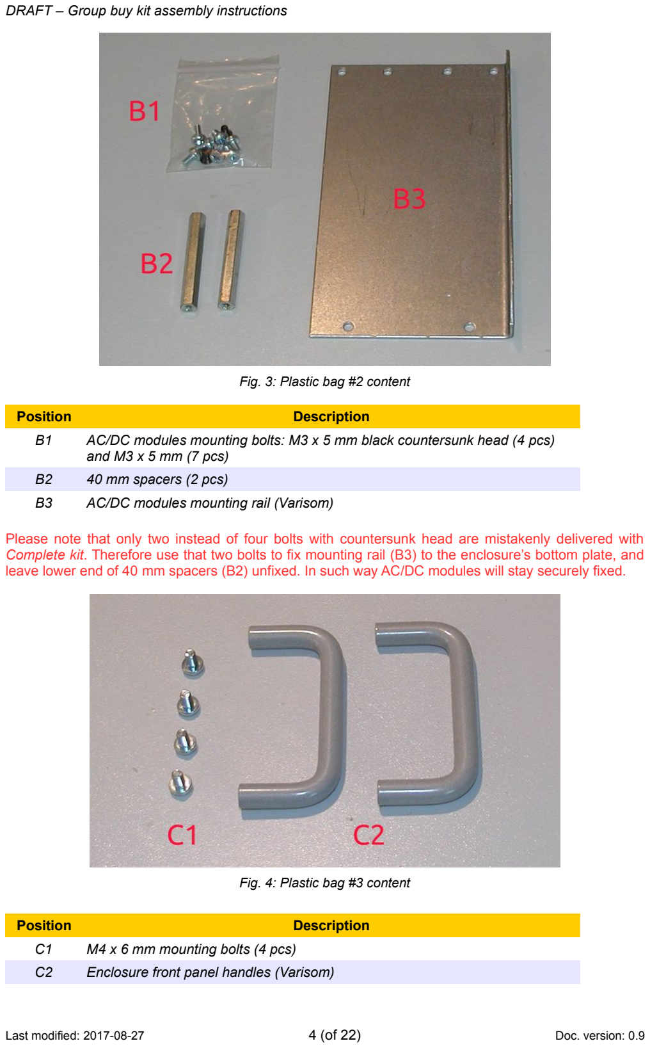
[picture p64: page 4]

Position | Description
B1 | AC/DC modules mounting bolts: M3 x 5 mm black countersunk head (4 pcs) and M3 x 5 mm (7 pcs)
B2 | 40 mm spacers (2 pcs)
B3 | AC/DC modules mounting rail (Varisom)

Please note that only two instead of four bolts with countersunk head are mistakenly delivered with Complete kit. Therefore use that two bolts to fix mounting rail (B3) to the enclosure’s bottom plate, and leave lower end of 40 mm spacers (B2) unfixed. In such way AC/DC modules will stay securely fixed.

Position | Description
C1 | M4 x 6 mm mounting bolts (4 pcs)
C2 | Enclosure front panel handles (Varisom)
Last modified: 2017-08-27 | 4 (of 22) | Doc. version: 0.9

Fig. 4: Plastic bag #3 content

Fig. 3: Plastic bag #2 content

Extra parts (for enclosure kit only)
This section is related only for buyers who ordered so-called Enclosure and Assemblies kit. It comes with few extra parts that together with the following items is required to get completely functional PSU:
- AC/DC modules (LRS-150-48 (http://www.tme.eu/en/details/lrs-150-48/industrial-power-supplies/mean-well/) or auto-switch LRS-150F-48) (http://www.tme.eu/en/details/lrs-150f-48/industrial-power-supplies/mean-well/) x2
- Assembled core modules (i.e. Aux power module, Power board x2, and Arduino Shield)
- 3.2” TFT color touchscreen display and
- Arduino Due compatible board

For more details please refer to EEZ PSU H24005 building instructions (r5B12). (http://www.envox.hr/eez/bench-power-supply/building-instructions.html)

Extra parts are shown on Fig. 5. Additionally a set of two custom made heatsinks are included into this kit.

Position | Description
G1 | 0.4 mm (for Q4) and 5 mm thermal silicone pads
G2 | Set of bolts for Power boards mounting to the heatsinks
G3 | 5 mm spacers for Power boards
G4 | 3.2” display mounting frame (Varisom) with bolts and 2 mm spacers
G5 | M3 x 5 mm bolts for display (4 pcs)
G6 | Set of fuses (230 Vac or 115 Vac as stated on cardboard box)
G7 | Encoder knob (A3116068) (http://www.tme.eu/en/details/a3116068/shaft-potentiometers-knobs/okw/) and knob cap (A3216007) (http://www.tme.eu/en/details/a3216007/shaft-potentiometers-knobs/okw/)

Bottom plate
In this step rubber feet (D1, Fig. 7) will be mounted and protective earth will be attached to the enclosure. Identify enclosure bottom plate using the Fig. 6 and prepare items A5 and A10.
Revision: 0.9 | 5 (of 22) | Last modified: 2017-08-27

Fig. 5: Extra parts for enclosure kit

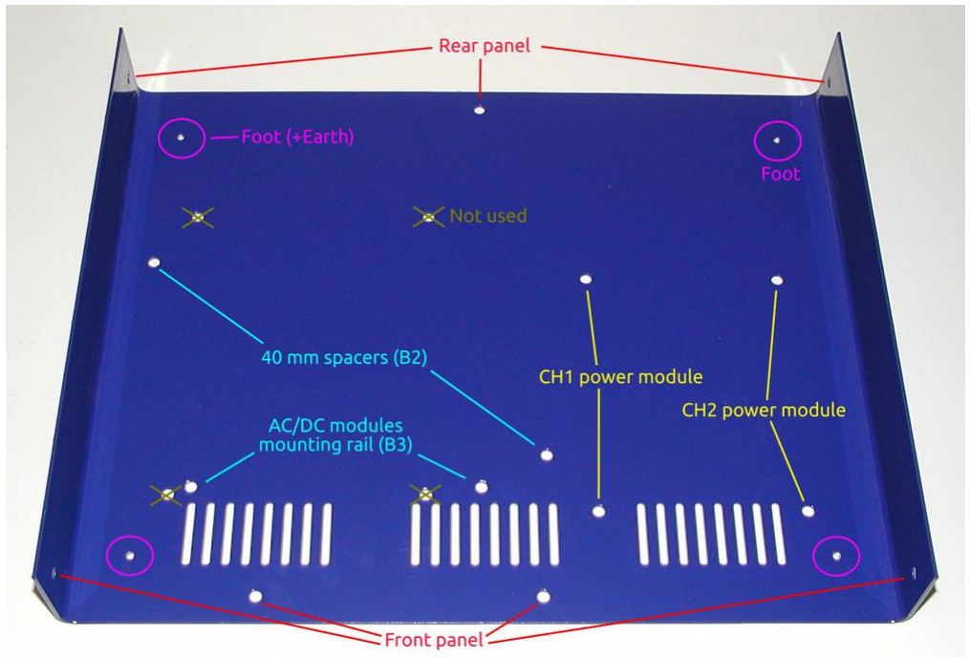
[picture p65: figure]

Content of A5 is shown on Fig. 7. Please note that longer bolt (D4) and additional parts (D5, D6) should be used for making contact with protective earth wire on the foot hole that is near the AC inlet (see note Foot (+Earth)).

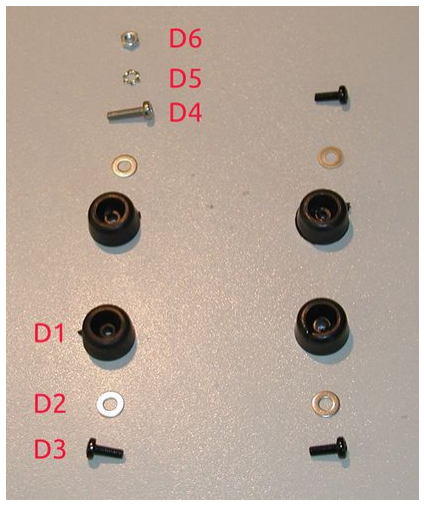
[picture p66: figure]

Use M3 black finish bolt (D3) and washer (D2) for mounting feet (D1) on the holes with M3 thread (see red circled hole on Fig. 9). The paint around latest hole where protection earth will be connected can be previously carefully removed to ensure even better electrical contact then externally serrated washer (D5) could provide (see Fig. 8).

Last modified: 2017-08-27 | 6 (of 22) | Doc. version: 0.9

Fig. 7: Enclosure feet package

Fig. 6: Enclosure bottom plate

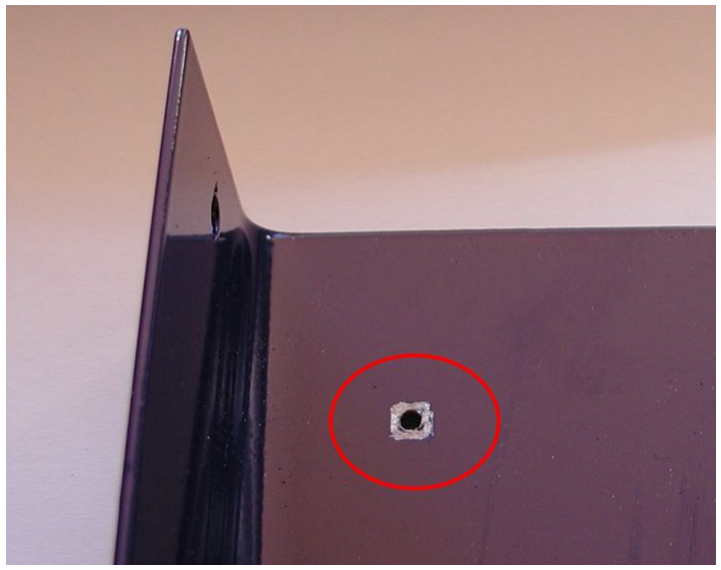
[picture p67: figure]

For protective earth connection mount last foot with long bolt (D4) first and then place ring terminal (item A10) on inner (top) side of the bottom plate between serrated washer (D5) and M3 nut (D6). Check with ohmmeter if low resistance connection is established between earth wire on A10 and bottom plate (when complete enclosure is assembled you can repeat this by testing conductance between earth pin on IEC AC inlet and top plate).
Fig. 9 shows bottom plate with protective earth mounted and Fig. 10 how robber foot looks like when mounted. Take into account that bolt should be screwed enough that its head is not above foot.

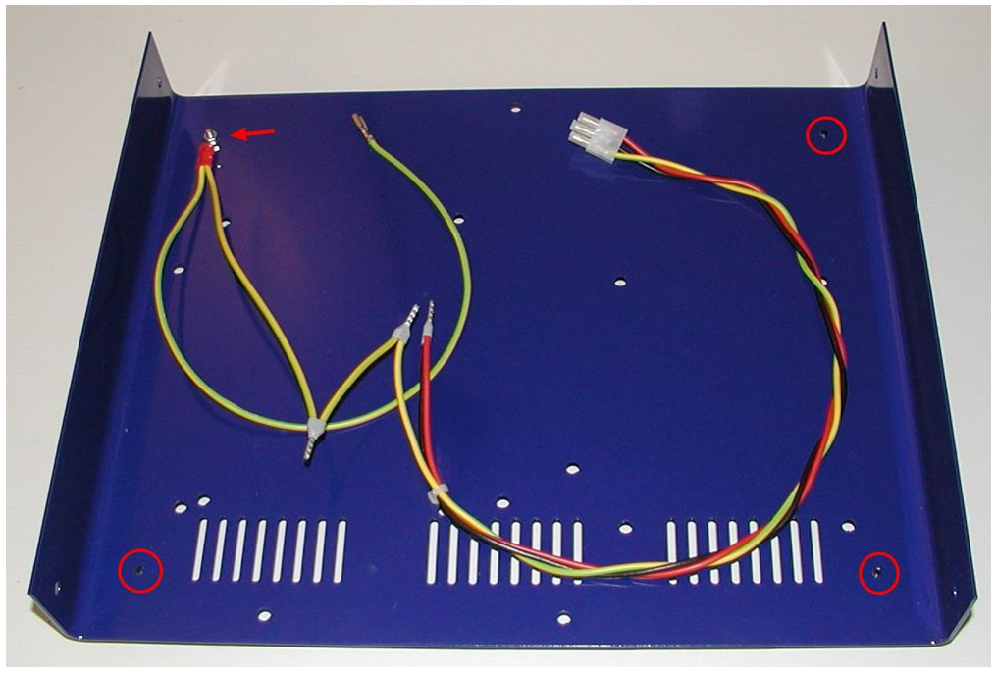
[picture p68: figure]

Revision: 0.9 | 7 (of 22) | Last modified: 2017-08-27

Fig. 8: Paint removed for better protective earth contact

Fig. 9: Bottom plate with mounted feet and protective earth

Rear panel

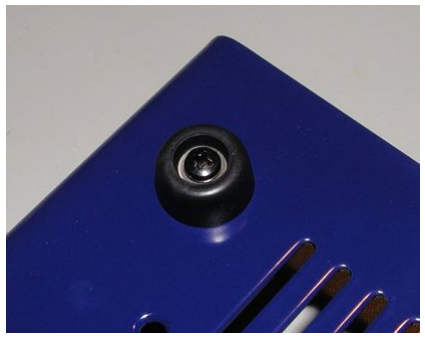
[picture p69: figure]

Remove rear panel from its cardboard box (item 3) and check if it looks as shown on Fig. 11. It should include IEC AC inlet (with AC switch patch cables (http://www.envox.hr/eez/bench-power-supply/wire-harness.html#ac_patch) that is not visible due to blue heatshrink tube), AUX power module with 5-pin AC plug and 3-pin cooling fan receptacle connected, 60 mm cooling fan and Cable set #2 (http://www.envox.hr/eez/bench-power-supply/wire-harness.html#cable_set2) connected.
The IEC AC Inlet has power switch and place for fuse drawer that carry two fuses. Fuse drawer is packed separately (item A4) and supplied two fuses (item E2, see Fig. 14) should be in accordance with AC mains voltage in your country (4 A for 230 Vac or 8 A for 115 Vac).

Do not insert fuse drawer with or without fuses before everything else is assembled.

If you didn’t notice any issues with rear panel parts you can proceed with mounting it to the previously prepared bottom plate by using three bolts from A7 and fix it into positions shown on Fig. 12.

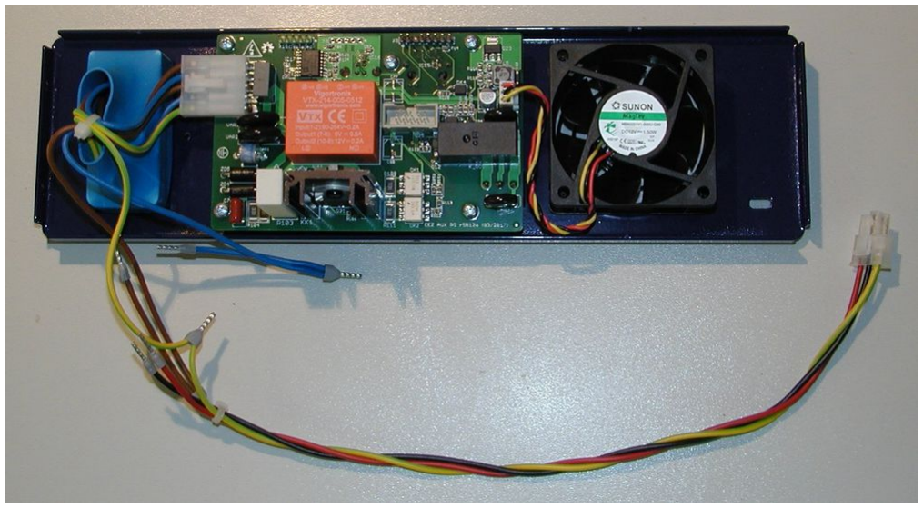
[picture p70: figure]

Last modified: 2017-08-27 | 8 (of 22) | Doc. version: 0.9

Fig. 10: Mounted rubber foot

Fig. 11: Rear panel assembled

Finally you can attach cables A1, A2 and A11 to the AUX power module as shown on Fig. 13.

AC/DC modules
Unpack box with AC/DC modules (item 5) and check if it contains items shown on Fig. 14.
Revision: 0.9 | 9 (of 22) | Last modified: 2017-08-27

Fig. 12: Rear panel mounting positions

Fig. 13: AUX power module wiring


Before proceed with assembly be sure that AC input voltage selection switch (Fig. 15) is properly set. This is especially important if your AC mains voltage is 230 Vac because if switch is set to 115 Vac it is possible that applied mains damage AC/DC module permanently (don’t count with blown fuses here!).

Put aside for the moment E2 and take one of E1 to connect on them Cable set #2 wires as follows:

Name | Position | Color
AC line input | L | Brown
AC neutral input | N | Blue
Protective earth | (Earth sign) | Yellow-green
DC output negative | -V | Black
DC output positive | +V | Red
Last modified: 2017-08-27 | 10 (of 22) | Doc. version: 0.9

Fig. 15: AC voltage selection switch set to 230 Vac

Fig. 14: AC/DC modules with fuses


Take also protective earth wire from Cable set #1 (item A10) and mount it on the same position as protective earth from Cable set #2 (see red cycle on Fig. 16).

When first (lower) AC/DC module wiring is completed you can proceed with fix it to the final place on the bottom plate by using two M3 bolts with black countersunk head (from B1) and metal spacers (B2).

Revision: 0.9 | 11 (of 22) | Last modified: 2017-08-27

Fig. 16: First (lower) AC/DC module wiring

Fig. 17: First (lower) AC/DC module fixing with metal spacers

Next step will be attaching AC/DC mounting rail (B3) with M3 bolts (from B1) to the AC/DC module and bottom plate as shown on Fig. 18. AC/DC module has three M3 holes on the side, only two bolts for mounting (red encircled), and another two with black countersunk head (also from B1) for fixing it at the bottom plate (see yellow arrows and Fig. 6).


Second AC/DC module can be now installed on top of the first (lower) one. First connect remaining wires from A10 and Cable set #2 as shown on Fig 20.
Before proceed with fixing second AC/DC module to mounting rail (B3), you can insert all cables that goes to Arduino Shield mounted on the front panel (see red encircled hole on Fig. 19 made by B3, two E1 and B2). You can use one of cable tie (A9) for that (spare another one for AUX temperature sensor A3).
Last modified: 2017-08-27 | 12 (of 22) | Doc. version: 0.9

Fig. 18: AC/DC modules mounting rail with first (lower) module


Use two M3 bolts from B1 for fix second (upper) AC/DC module on the side. Use another M3 bolt for fix it only on the spacer B2 that is visible on Fig. 18. Fixing on the next spacer will be performed in the next step.

Revision: 0.9 | 13 (of 22) | Last modified: 2017-08-27

Fig. 19: Second (upper) AC/DC module with Arduino Shield wiring


Final step in AC/DC modules mounting is to put a cover (item A6) over second (upper) AC/DC module terminals as an additional safety measure against electric shock when you decide for any reason to operate the PSU with top plate removed. Use two remaining M3 bolts (from B1) and fix it on the places marked with red arrows on Fig. 21.

Last modified: 2017-08-27 | 14 (of 22) | Doc. version: 0.9

Fig. 20: Second (upper) AC/DC module mounting

Fig. 21: Second (upper) AC/DC module terminal cover


Front panel
The front panel box content is shown on Fig. 22 that is enclosure’s front panel with mounted Arduino Shield (http://www.envox.hr/eez/bench-power-supply/psu-digital-control.html) with Arduino Due board, 3.2” TFT touchscreen color display and 4 mm binding posts for power outputs and protective earth.

A first step for the front panel assembly is mounting of handles (item C2). Use two M4 bolts (C1) to fix it on the front panel’s ends. Fig. 23 shows how front panel looks like with handles mounted.

Revision: 0.9 | 15 (of 22) | Last modified: 2017-08-27

Fig. 22: Front panel (back view)

Fig. 23: Front panel handles mounted

Attach the front panel very loosely to the bottom cover to avoid issue with mounting Power boards lately (see issue #52). (https://github.com/eez-open/psu-hw/issues/52)

A next step should be wiring of the Arduino Shield (use red colored text on Fig. 22 as reference). That also include AUX temperature sensor (item A3). Take a special care when inserting USB cable (A11) to the Programming port (lower one) on the Arduino Due to not damage micro USB socket. It’s recommended to bend USB cable appropriately before insertion to lower its pressure when it is put into place (Fig. 25).

Use Native port (upper one) with firmware v1.01 or latter. If you still want to use programming port add the following code into your conf_user.h file:

#undef CONF_SERIAL_USE_NATIVE_USB_PORT

#define CONF_SERIAL_USE_NATIVE_USB_PORT 0


Use four M3 bolts (from A7) to join front panel with bottom plate following the holes marked on Fig. 6 and Fig. 26

Last modified: 2017-08-27 | 16 (of 22) | Doc. version: 0.9

Fig. 25: USB cable attached to Arduino Due programming port

Fig. 24: Arduino Shield with cables connected


When front panel is mounted to the bottom plate it’s possible to fix AUX temperature sensor (A3) someplace above AC/DC modules as shown on Fig. 27. Use one cable tie (A9) for that.


Power boards
The Power boards cardboard box contains two Power boards (F1) and M3 bolts (F2) used for mounting. Before mounting power boards to the bottom plate (check Fig. 6) plug in the DC power cable (+48 V) to the DC input connector (red encircled on Fig. 29).

Now you can carefully insert it into Arduino Shield (Fig. 21) that PCB components side is facing toward cooling fan center as shown on Fig. 30. Double check that no misalignment between 26-pin header on the Arduino Shield and Power board’s receptacle (yellow encircled on Fig. 28) exists.

Revision: 0.9 | 17 (of 22) | Last modified: 2017-08-27

Fig. 27: Aux temperature sensor

Fig. 26: Front panel bottom mounting positions


Final steps
The PSU with all parts mounted is shown on Fig. 30. Covering it with top plate and placing fuses into AC inlet is now only what is left.

You’ll need eight M3 bolts with black countersunk head (from A7 and F2) for mounting top plate.

Last modified: 2017-08-27 | 18 (of 22) | Doc. version: 0.9

Fig. 28: Power boards unpackaged

Fig. 29: Power board DC input connector


Check fuses (E2) rating (i.e. 8 A for 115 Vac and 4 A for 230 Vac) before placing them into fuse drawer (A4) as shown on Fig. 31.

Mount fuse drawer into IEC AC inlet on the rear panel and insert AC mains power cord (it’s not a part of this kit!) as shown on Fig. 32.

Revision: 0.9 | 19 (of 22) | Last modified: 2017-08-27

Fig. 30: EEZ H24005 assembled without top plate

Fig. 31: Fuse drawer


The PSU has on the rear panel a 3-pin connector for Digital out #2 (DOUT2). You can use A8 plug with screw terminals to make connection with external circuits (Fig. 33).

The PSU complete kit comes with firmware v1.0 loaded into Arduino Due board. For further uploads please follow instructions here. (http://www.envox.hr/eez/bench-power-supply/building-instructions.html#instr_fw) The list of firmware release can be found on the GitHub. (https://github.com/eez-open/psu-firmware/releases)

Powering up, calibration and firmware upload
Do not start PSU for the first time with any load connected!

First test output voltage programming. When set output voltage is within expected tolerance (i.e. up to 5 % not calibrated) you can continue with testing output current capability. Choose output voltage and load combination that output current at start is not higher then e.g. 100 mA. If reading is within expected

Last modified: 2017-08-27 | 20 (of 22) | Doc. version: 0.9

Fig. 32: AC inlet with fuse drawer and plugged in power cord

Fig. 33: DOUT2 plug-in connector tolerance, you can proceed with higher load up to 5 A per channel.

The Power board outputs are not calibrated. At the first start you will be asked about calibration but you can postpone it. Each output has to be calibrated separately and you can access calibration wizard from System page or from Channel’s info page (Fig. 34).


The calibration wizard will guide you through all steps after you successfully entered calibration password (default is eezpsu). Voltage set for current calibration is 20 V (middle of the range) therefore you have to use resistor lower then 4 Ω that can dissipate enough power (example1, (http://www.tme.eu/en/details/ax50wr-1r/50w-resistors/te-connectivity/2-1625984-2/) example2 (http://www.tme.eu/en/details/ax100wr-3r3/100w-resistors/te-connectivity/3-1625999-3/) both of them must be installed on heatsink!).
Please note that high current (5 A) range calibration could be a rather tricky since output current is going to decrease over time as shunt resistor is heating up. That is a known issue (see hardware issue #40 (https://github.com/eez-open/psu-hw/issues/40) and suggestion for compensation in firmware reported in #100). (https://github.com/eez-open/psu-firmware/issues/100) Depends of what end result is more acceptable, you can enter output current value that is measured immediately after the load is connected, or you can wait up to few minutes (e.g. before fan is started to work) and measure the output current.

Troubleshooting

- Display is not working – during displays testing we found on considerable number of them that they pins have to be degreased. It’s possible that your display’s pins are not degreased enough, or lost contact due to mechanical shocks in transportation. Detach it from front panel and Arduino Shield board first, and try to clean pins with cleaning/degreasing spray (e.g. Kontakt WL). (http://www.tme.eu/en/details/wl_200/cleaning-maintaining-products/kontakt-chemie/71009-002/) Pay special attention to make sure that cleaning agent not penetrate between display and it’s PCB. That could create a visible spot when display is turned on (if cleaning agent is not aggressive that should be a temporary issue. Wait some time that cleaning agent simply evaporate).
- Display colors are “washed out” – it appears that for used “noname” display backlight and colors intensity could vary considerably. While testing we found about half of dozen different level of backlight intensity. We tried to rectify that to some extend by offering display brightness and background color (i.e. the blue one) luminosity settings. You can find that parameters under system settings page 2 as shown on Fig. 35. We tried to set the most appropriate luminosity level for your display. The default value is 15 but if your found here e.g. 10 (for firmware v1.0) that means that your display is unfortunately is too bright (hence lower value). In that case the real “cure” is to start hunting for better unit on eBay or similar online shops.


- Output voltage is above max. range (e.g. 42-43 V) – voltage regulation is failed, possibly due
Revision: 0.9 | 21 (of 22) | Last modified: 2017-08-27

Fig. 34: Channel's calibration page

Fig. 35: Display settings page (firmware v1.01)

to faulty bias power supply. Switch the PSU off immediately and check V+ and V- outputs of IC4 (on ferrite beads FB2 and FB3). It’s highly possible that IC4 thermal pad is not soldered properly and that mechanical shock (e.g. in transportation) cause lost of electrical contact. It’s output voltage has to be a little above 5 V (if you’re perfectionist replace R20 and R25 with 316 K), but if IC4’s thermal pad, that is also its ground connection, is not connected you can expected e.g. about +12 V on V+ and -0.5 V on V- line. If that happen it’s also possible that IC12 is damaged permanently (start up self-test procedure will report DAC failure in that case). Another possible collateral damage could happed if load is mistakenly connected. That can easily damage low current switch and sense resistor (Q13 and R63).
If IC4 reflow soldering work is necessary detach PCB from the heatsink and remove thermal pads first!
- Output current cannot reach max. value (i.e. 5 A) with load connected – if Power board output cannot deliver max. current for more then 10 seconds or cannot reach max. current with output current step is programmed (e.g. from 0 to 5 A) then probably something is wrong with switching pre-regulator on the first place. We found on dozen of Power boards that came from manufacturer that C14 is not soldered properly or is dropped off the PCB. Without it pre-regulator cannot manage to deliver more then about 3 A. Another possibility is that IC1 thermal pad is not properly soldered (similar to above mentioned IC4). You have to be ready for some resoldering work with hot air. If max. output current cannot reach more then 1.5 A please check Q13 and Q14 first, before going to do anything with IC1. Even if you need to desolder them for testing purposes it’s still less cumbersome then resoldering IC1.
If IC1 reflow soldering work is necessary detach PCB from the heatsink and remove thermal pads first!
- USB cable is shutting down a whole unit – unfortunately your USB patch cable is faulty. Please check wiring pin by pin (i.e. check if red wire is connected with +VUSB, black with GND, etc.).
It’s possible that you have to rotate it as one user suggested as shown on Fig. 36. If that is not acceptable, you can try to detach pin by pin from the header and put them on the right place.


- Channel enters unregulated mode (neither CV nor CC when output value is displayed in red color) for programmed output voltage below ~1.8 V. Replace R20 and R25 with 316 K as suggested in issue #42 (https://github.com/eez-open/psu-hw/issues/42) on the GitHub.
- Output current cannot reach max. value of 5 A on step load – that can be check by set output enable with connected load, or by connecting load when output is already enabled. Make sure that used load is low enough that channel enters CC mode. For example use 3.3 Ω with output set to 20 V and current set to maximum. Try to replace pre-regulator current sense resistor R4 with another one (we found on few boards that comes from manufacturer that R4 resistance is too high despite the fact that marked value is correct (i.e. 10 mΩ).

A work in progress

Last modified: 2017-08-27 | 22 (of 22) | Doc. version: 0.9

Fig. 36: Swapped USB connector

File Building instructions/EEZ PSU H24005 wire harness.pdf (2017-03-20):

EEZ PSU H24005 wire harness

## EEZ PSU H24005 wire harness

- Ethernet cable
- Cooling fan cable
- AUX temperature sensor cable
- AC switch patch cables
- Cable set #1
- Cable set #2
- Pre-assembled cables
- BOM

EEZ PSU H24005 Wire harness

### 1. Ethernet cable

Total length | 250 (± 5) mm
Type | 4 pairs Ethernet, stranded wire
TME | HELUKAT100-FTP-FP (http://www.tme.eu/en/details/helukat100-ftp-fp/telecommunication-cables/helukabel/80055/) or e.g. cut CA00600.00C01 (http://www.tme.eu/en/details/ca00600.00c01/rj45-cables/belden/) to size
Farnell | 1602385 (http://export.farnell.com/draka/900221va0000fe0100/cable-patch-5e-utp-grey-100m/dp/1602385) or e.g. cut 1734894 (http://export.farnell.com/pro-signal/ps11029/patch-lead-5e-0-5m-grey/dp/1734894) to size
| | Connectors
Side A | X8 | Side B | X18
Housing type | Receptacle, 0.1” | Housing type | See side A
TME | NSR-08 (http://www.tme.eu/en/details/nsr-08/pin-headers/ninigi/) | TME | See side A
Farnell | 865667 (http://export.farnell.com/harwin/m20-1060800/crimp-housing-8way/dp/865667) | Farnell | See side A
Pin: | Female | Pin | See side A
Pin quantity | 8 | Pin quantity | 7
TME | NDR-T (http://www.tme.eu/en/details/ndr-t/pin-headers/ninigi/) | TME | See side A
Farnell | 1022219 (http://export.farnell.com/harwin/m20-1180042/crimp-socket-gold-22-30awg-pk100/dp/1022219) | Farnell | See side A
Polarising key | Position #3
TME | NSDR-KEY (http://www.tme.eu/en/details/nsdr-key/pin-headers/ninigi/)
Farnell | 512023 (http://export.farnell.com/harwin/m20-003/polarising-key-pk100/dp/512023)

Wiring

Name | Position | Color / description | Position | Color / description
LED link | 1 | Brown-white | 1 | Brown-white
LED act | 2 | Brown | 2 | Brown
Shield | 3 | Blue-white | 3 | Polarising key
RX+ | 4 | Orange-white | 4 | Orange-white
RX- | 5 | Orange | 5 | Orange
TX+ | 6 | Green-white | 6 | Green-white
TX- | 7 | Green | 7 | Green
+3.3V | 8 | Blue | 8 | Blue

Picture


### 2. Cooling fan cable

Total length | 100 (± 5) mm
Type | 3 wire, already mounted on the cooling fan
Fan: | TME: MB60251V1-G99 (http://www.tme.eu/en/details/mb60251v1-g99/dc12v-fans/sunon/mb60251v1-000u-g99/)

Connectors
Side A | X6 | Side B | N/A
Housing type | Receptacle, 0.1” | Housing type | N/A
TME | MX-6471-031 (http://www.tme.eu/en/details/mx-6471-031/raster-signal-connectors-254mm/molex/022012035-22-01-2035-6471-03i/) | TME | N/A
Farnell | 143127 (http://export.farnell.com/molex/22-01-2035/crimp-housing-2-54mm-3way/dp/143127) | Farnell | N/A
Pin | Female | Pin | N/A
Pin quantity | 3 | Pin quantity | 0
TME | MX-0850-0114 (http://www.tme.eu/en/details/mx-0850-0114/raster-signal-connectors-254mm/molex/008500114-08-50-0114-2759-p909l/) | TME | N/A
Farnell | 2063734 (http://export.farnell.com/molex/08-50-0113/contact-crimp-terminal-30-22awg/dp/2063734) | Farnell | N/A

Additional info
Fan is already equipped with cable that has to be cut to size and terminated with connector

Wiring
Name | Position | Color / description
12 Vdc | 1 | Red
GND | 2 | Black
Sense | 3 | Yellow

Picture


### 3. AUX temperature sensor cable

Total length | 145 (± 5) mm
Type | Max. 0.35 mm²
singe wire, stranded
TME | E.g. brown: LGY0.35/25-BR (http://www.tme.eu/en/details/lgy0.35_25-br/single-core-cable-strand/bq-cable/) (or any other color)
Farnell | E.g. brown: 2425402 (http://export.farnell.com/pro-power/mc6a-7-0-2t2-bn-100/equipment-wire-0-22mm2-brown-per/dp/2425402) (0.22 mm²
| | )
NTC | TME: NTCLE100E3103JB0, (http://www.tme.eu/en/details/ntcle100e3103jb0/tht-measurement-ntc-thermistors/vishay/) Farnell: 1187031 (http://export.farnell.com/vishay/ntcle100e3103jb0/thermistor-10k-5-ntc-rad/dp/1187031)
Wire | TME: LGY0.35/25-BR, (http://www.tme.eu/en/details/lgy0.35_25-br/single-core-cable-strand/bq-cable/) Farnell: 2425402 (http://export.farnell.com/pro-power/mc6a-7-0-2t2-bn-100/equipment-wire-0-22mm2-brown-per/dp/2425402)
| | Connectors
Side A | X17 | Side B | N/A
Housing type | Receptacle 0.1” | Housing type | N/A
TME | MX-6471-021 (http://www.tme.eu/en/details/mx-6471-021/raster-signal-connectors-254mm/molex/022012025-22-01-2025-6471-02i/) | TME | N/A
Farnell | 143126 (http://export.farnell.com/molex/22-01-2025/crimp-housing-2-54mm-2way/dp/143126) | Farnell | N/A
Pin | Female | Pin | N/A
Pin quantity | 2 | Pin quantity | 0
TME | MX-0850-0114 (http://www.tme.eu/en/details/mx-0850-0114/raster-signal-connectors-254mm/molex/008500114-08-50-0114-2759-p909l/) | TME | N/A
Farnell | 2063734 (http://export.farnell.com/molex/08-50-0113/contact-crimp-terminal-30-22awg/dp/2063734) | Farnell | N/A

Additional info
The temperature sensor is already equipped with cable that has to be terminated with connector

Wiring
Name | Position | Color / description
MCU_VCC 1 | Any color
NTC | 2 | Any color

Picture


### 4. AC switch patch cables

Total length | 45 (± 5) mm
Type | 0.75 mm²
singe wire, stranded, min. 250 VAC
TME | Brown: LGY0.75/25-BR, (http://www.tme.eu/en/details/lgy0.75_25-br/single-core-cable-strand/bq-cable/) Blue: LGY0.75/25-BL (http://www.tme.eu/en/details/lgy0.75_25-bl/single-core-cable-strand/bq-cable/)
Farnell | Brown: 2528103, (http://export.farnell.com/pro-power/pp001205/tri-rated-wire-0-75mm2-brown-1m/dp/2528103) Blue: 2528092 (http://export.farnell.com/pro-power/pp001196/tri-rated-wire-0-75mm2-blue-1m/dp/2528092)
Connectors
Side A | AC output | Side B | AC Switch input
Pin | Female quick discon- nect | Pin | See side A
Pin quantity | 2 | Pin quantity | See side A
TME | BM01148 (http://www.tme.eu/en/details/bm01148/non-insulated-terminals/bm-group/bm-01148/) or ST-003/2 (http://www.tme.eu/en/details/st-003_2/non-insulated-terminals/ninigi/) | TME | See side A
Farnell | 3625424 (http://export.farnell.com/jst-japan-solderless-terminals/sto-1-0t-187n-8/terminal-female-4-8x0-8mm/dp/3625424) | Farnell | See side A

Additional info
Required for Schurter 4304.6090 (http://www.tme.eu/en/details/4304.6090/ac-power-connectors/schurter/) IEC inlet (C14, 6765, 10A)

Wiring1
Name | Position | Color / description | Position | Color / description
Line | 1 | Brown | 1 | Brown

Wiring2
Name | Position | Color / description | Position | Color / description
Neutral | 1 | Blue | 1 | Blue
Picture


### 5. Cable set #1

### 5.1. Section A: Power board (CH2) X1 cable

Length | 420 (± 5) mm
Type | 0.75 mm²
singe wire, stranded, min. 250 VAC
TME | Red: LGY0.75/25-RD, (http://www.tme.eu/en/details/lgy0.75_25-rd/single-core-cable-strand/bq-cable/) Black: LGY0.75/25-BK (http://www.tme.eu/en/details/lgy0.75_25-bk/single-core-cable-strand/bq-cable/) Green-Yellow: LGY0.75/25-YL/GR (http://www.tme.eu/en/details/lgy0.75_25-yl_gr/single-core-cable-strand/bq-cable/)
Farnell | Red: 2528175, (http://export.farnell.com/pro-power/pp001270/tri-rated-wire-0-75mm2-red-1m/dp/2528175) Black: 2528082, (http://export.farnell.com/pro-power/pp001186/tri-rated-wire-0-75mm2-black-1m/dp/2528082) Green-Yellow: 2528140 (http://export.farnell.com/pro-power/pp001239/tri-rated-wire-0-75mm2-grn-yellow/dp/2528140)
Connectors
Side A | Power board X1 (Ch2) | Side B | AC/DC module power output
Housing type | Male, Mini-Fit Jr. | Housing type | Ferrule, single wire
TME | MX-5557-03R2 (http://www.tme.eu/en/details/mx-5557-03r2/raster-signal-connectors-420mm/molex/039014030-39-01-4030-5557-03r2/) | TME | H0.75/14D/GY (http://www.tme.eu/en/details/h0.75_14d_gy/bootlace-ferrules/weidmuller/9019040000-h07514d-gr/)
Farnell | 9963480 (http://export.farnell.com/molex/39-01-4030/crimp-housing-rcpt-sil-3way-mini/dp/9963480) | Farnell | 841195 (http://export.farnell.com/weidmuller/h0-75-14/ferrule-insulated-0-75mm-white/dp/841195)
Pin | Female | Quantity | 2
Pin quantity | 3 | Housing type | Ferrule, twin entry
TME | MX-5556-T3L (http://www.tme.eu/en/details/mx-5556-t3l/raster-signal-connectors-420mm/molex/039000078-39-00-0078-5556t3l/) | TME | H0.75/15D2/GY (http://www.tme.eu/en/details/h0.75_15d2_gy/bootlace-ferrules/weidmuller/9037410000-h07514d-zh-gr/)
Farnell | 9732675 (http://export.farnell.com/molex/39-00-0078/crimp-socket-16awg-pk100/dp/9732675) | Farnell | 1121751 (http://export.farnell.com/weidmuller/9037410000/ferrule-twin-entry-0-75mm/dp/1121751)

Quantity | 1
Wiring
Name | Position | Color / description | Position | Color / description
Earth | 1 | Green-Yellow | N/A | Ferrule, twin entry
Vin- | 2 | Black | N/A | Ferrule
Vin+ | 3 | Red | N/A | Ferrule

### 5.2. Section B: AC/DC module Earth

Length | 70 (± 1) mm
Type | 0.75 mm²
singe wire, stranded, min. 250 VAC
TME | LGY0.75/25-YL/GR (http://www.tme.eu/en/details/lgy0.75_25-yl_gr/single-core-cable-strand/bq-cable/)
Farnell | 2528140 (http://export.farnell.com/pro-power/pp001239/tri-rated-wire-0-75mm2-grn-yellow/dp/2528140)
Connectors
Side A | AC/DC module Earth output | Side B | AC/DC module Earth (in)
Housing type | Use twin entry ferrule, See B
side, Section A
Housing type | Ferrule, twin entry
TME | H0.75/15D2/GY (http://www.tme.eu/en/details/h0.75_15d2_gy/bootlace-ferrules/weidmuller/9037410000-h07514d-zh-gr/)
Farnell | 1121751 (http://export.farnell.com/weidmuller/9037410000/ferrule-twin-entry-0-75mm/dp/1121751)
| | Quantity | 1

### 5.3. Section C: Chassis Earth

Length: | 170 (± 5) mm
Type: | 0.75 mm²
singe wire, stranded, min. 250 VAC
TME | LGY0.75/25-YL/GR (http://www.tme.eu/en/details/lgy0.75_25-yl_gr/single-core-cable-strand/bq-cable/)
Farnell | 2528140 (http://export.farnell.com/pro-power/pp001239/tri-rated-wire-0-75mm2-grn-yellow/dp/2528140)
| | Connectors
Side A | AC/DC module Earth (in) | Side B | Chassis Earth (bottom plate)
Housing type | Use twin entry ferrule, See B side, Section B | Housing type | Non-insulated, Ring terminal, 3 mm
| | TME | BM 91103 (http://www.tme.eu/en/details/bm91103/non-insulated-terminals/bm-group/bm-91103/)
| | Farnell | 7356528 (http://export.farnell.com/jst-japan-solderless-terminals/lrb-1-0t-m3/crimp-terminal-ring-m3/dp/7356528)
Quantity | 1

### 5.4. Section D: Arduino Shield Earth

Length: | 350 (± 5) mm
Type: | 0.75 mm²
singe wire, stranded, min. 250 VAC
TME | LGY0.75/25-YL/GR (http://www.tme.eu/en/details/lgy0.75_25-yl_gr/single-core-cable-strand/bq-cable/)
Farnell | 2528140 (http://export.farnell.com/pro-power/pp001239/tri-rated-wire-0-75mm2-grn-yellow/dp/2528140)
Connectors
Side A | Chassis Earth (bottom plate) | Side B | Arduino Shield Earth input (J3)
Housing type | Use ring terminal, See B side, Section C | Housing type | Female quick disconnect
| | TME | BM01148 (http://www.tme.eu/en/details/bm01148/non-insulated-terminals/bm-group/bm-01148/) or ST-003/2 (http://www.tme.eu/en/details/st-003_2/non-insulated-terminals/ninigi/)
| | Farnell | 3625424 (http://export.farnell.com/jst-japan-solderless-terminals/sto-1-0t-187n-8/terminal-female-4-8x0-8mm/dp/3625424)
Quantity | 1

### 6. Cable set #2


### 6.1. Section A: Power board X1 cable

Length | 330 (± 5) mm
Type | 0.75 mm²
singe wire, stranded, min. 250 VAC
TME | Red: LGY0.75/25-RD, (http://www.tme.eu/en/details/lgy0.75_25-rd/single-core-cable-strand/bq-cable/) Black: LGY0.75/25-BK (http://www.tme.eu/en/details/lgy0.75_25-bk/single-core-cable-strand/bq-cable/) Green-Yellow: LGY0.75/25-YL/GR (http://www.tme.eu/en/details/lgy0.75_25-yl_gr/single-core-cable-strand/bq-cable/)
Farnell | Red: 2528175, (http://export.farnell.com/pro-power/pp001270/tri-rated-wire-0-75mm2-red-1m/dp/2528175) Black: 2528082, (http://export.farnell.com/pro-power/pp001186/tri-rated-wire-0-75mm2-black-1m/dp/2528082) Green-Yellow: 2528140 (http://export.farnell.com/pro-power/pp001239/tri-rated-wire-0-75mm2-grn-yellow/dp/2528140)
Connectors
Side A | Power board X1 (Ch1) | Side B | AC/DC module power output

Housing type | Male, Mini-Fit Jr. | Housing type | Ferrule, single wire
TME | MX-5557-03R2 (http://www.tme.eu/en/details/mx-5557-03r2/raster-signal-connectors-420mm/molex/039014030-39-01-4030-5557-03r2/) | TME | H0.75/14D/GY (http://www.tme.eu/en/details/h0.75_14d_gy/bootlace-ferrules/weidmuller/9019040000-h07514d-gr/)
Farnell | 9963480 (http://export.farnell.com/molex/39-01-4030/crimp-housing-rcpt-sil-3way-mini/dp/9963480) | Farnell | 841195 (http://export.farnell.com/weidmuller/h0-75-14/ferrule-insulated-0-75mm-white/dp/841195)


Pin | Female | Quantity | 2
Pin quantity | 3 | Housing type | Ferrule, twin entry
TME | MX-5556-T3L (http://www.tme.eu/en/details/mx-5556-t3l/raster-signal-connectors-420mm/molex/039000078-39-00-0078-5556t3l/) | TME | H0.75/15D2/GY (http://www.tme.eu/en/details/h0.75_15d2_gy/bootlace-ferrules/weidmuller/9037410000-h07514d-zh-gr/)
Farnell | 9732675 (http://export.farnell.com/molex/39-00-0078/crimp-socket-16awg-pk100/dp/9732675) | Farnell | 1121751 (http://export.farnell.com/weidmuller/9037410000/ferrule-twin-entry-0-75mm/dp/1121751)
Quantity | 1

Wiring:

Name | Position | Color / description | Position | Color / description
Earth | 1 | Green-Yellow | N/A | Ferrule, twin entry
Vin- | 2 | Black | N/A | Ferrule
Vin+ | 3 | Red | N/A | Ferrule

### 6.2. Section B: AC/DC module Earth

Length | 165 (± 5) mm
Type | 0.75 mm²
singe wire, stranded, min. 250 VAC
TME | LGY0.75/25-YL/GR (http://www.tme.eu/en/details/lgy0.75_25-yl_gr/single-core-cable-strand/bq-cable/)
Farnell | 2528140 (http://export.farnell.com/pro-power/pp001239/tri-rated-wire-0-75mm2-grn-yellow/dp/2528140)
Connectors
Side A | AC/DC power module Earth (in) Side B | AC inlet Earth
Housing type | Use twin entry ferrule, See B
side from Section A
Housing type | Female quick disconnect
Quantity | 1
TME | BM01148 (http://www.tme.eu/en/details/bm01148/non-insulated-terminals/bm-group/bm-01148/) or ST-003/2 (http://www.tme.eu/en/details/st-003_2/non-insulated-terminals/ninigi/)
Farnell | 3625424 (http://export.farnell.com/jst-japan-solderless-terminals/sto-1-0t-187n-8/terminal-female-4-8x0-8mm/dp/3625424)

### 6.3. Section C: AUX PS module Earth

Length | 115 (± 5) mm
Type | 0.75 mm²
singe wire, stranded, min. 250 VAC
TME | LGY0.75/25-YL/GR (http://www.tme.eu/en/details/lgy0.75_25-yl_gr/single-core-cable-strand/bq-cable/)
Farnell | 2528140 (http://export.farnell.com/pro-power/pp001239/tri-rated-wire-0-75mm2-grn-yellow/dp/2528140)
| | Connectors
Side A | AC inlet Earth | Side B | AUX PS module (X3)
Housing type | Use Female quick disconnect terminal, See B side, Section B | Housing type | Male, Mini-Fit Jr.
| | TME | MX-5557-05R2 (http://www.tme.eu/en/details/mx-5557-05r2/raster-signal-connectors-420mm/molex/039014050-39-01-4050-5557-05r2/)
| | Farnell | 9963502 (http://export.farnell.com/molex/39014050/crimp-housing-rcpt-sil-5way-mini/dp/9963502)
Pin | Female
Pin quantity | 5
TME | MX-5556-T3L (http://www.tme.eu/en/details/mx-5556-t3l/raster-signal-connectors-420mm/molex/039000078-39-00-0078-5556t3l/)
Farnell | 9732675 (http://export.farnell.com/molex/39-00-0078/crimp-socket-16awg-pk100/dp/9732675)

Wiring:

Name | Position | Color / description | Position | Color / description
– | – | Female quick disconnect | 1 | Earth

### 6.4. Section D: Lower AC/DC module power input

Length | 200 (± 5) mm
Type | 0.75 mm²
singe wire, stranded, min. 250 VAC
TME | Brown: LGY0.75/25-BR, (http://www.tme.eu/en/details/lgy0.75_25-br/single-core-cable-strand/bq-cable/) Blue: LGY0.75/25-BL (http://www.tme.eu/en/details/lgy0.75_25-bl/single-core-cable-strand/bq-cable/)
Farnell | Brown: 2528103, (http://export.farnell.com/pro-power/pp001205/tri-rated-wire-0-75mm2-brown-1m/dp/2528103) Blue: 2528092 (http://export.farnell.com/pro-power/pp001196/tri-rated-wire-0-75mm2-blue-1m/dp/2528092)
| | Connectors
Side A | AUX PS module (X3) | Side B | Lower AC/DC module power input
Housing type | See Side B, Section C | Housing type Ferrule, twin entry
TME | - | TME | H0.75/15D2/GY (http://www.tme.eu/en/details/h0.75_15d2_gy/bootlace-ferrules/weidmuller/9037410000-h07514d-zh-gr/)
Farnell | - | Farnell | 1121751 (http://export.farnell.com/weidmuller/9037410000/ferrule-twin-entry-0-75mm/dp/1121751)
Pin | Female | Quantity | 2
Pin quantity | 2
TME | MX-5556-T3L (http://www.tme.eu/en/details/mx-5556-t3l/raster-signal-connectors-420mm/molex/039000078-39-00-0078-5556t3l/)
Farnell | 9732675 (http://export.farnell.com/molex/39-00-0078/crimp-socket-16awg-pk100/dp/9732675)

Wiring:

Name | Position | Color / description | Position | Color / description
Neutral | 2 | Blue | N/A | Ferrule, twin entry
Line | 3 | Brown | N/A | Ferrule, twin entry

### 6.5. Section E: Upper AC/DC module power input

Length | 75 (± 1) mm
Type | 0.75 mm²
singe wire, stranded, min. 250 VAC
TME | Brown: LGY0.75/25-BR, (http://www.tme.eu/en/details/lgy0.75_25-br/single-core-cable-strand/bq-cable/) Blue: LGY0.75/25-BL (http://www.tme.eu/en/details/lgy0.75_25-bl/single-core-cable-strand/bq-cable/)
Farnell | Brown: 2528103, (http://export.farnell.com/pro-power/pp001205/tri-rated-wire-0-75mm2-brown-1m/dp/2528103) Blue: 2528092 (http://export.farnell.com/pro-power/pp001196/tri-rated-wire-0-75mm2-blue-1m/dp/2528092)
Connectors
Side A | Lower AC/DC module power input Side B | Upper AC/DC module power input
Housing type Use twin entry ferrule, See B side,
Section D

Housing type Ferrule, single wire

TME | H0.75/14D/GY (http://www.tme.eu/en/details/h0.75_14d_gy/bootlace-ferrules/weidmuller/9019040000-h07514d-gr/)
Farnell | 1121751 (http://export.farnell.com/weidmuller/9037410000/ferrule-twin-entry-0-75mm/dp/1121751)

| | Quantity | 2

### 6.6. Section F: AUX PS module power input

Length | 110 (± 5) mm
Type | 0.75 mm²
singe wire, stranded, min. 250 VAC
TME | Brown: LGY0.75/25-BR, (http://www.tme.eu/en/details/lgy0.75_25-br/single-core-cable-strand/bq-cable/) Blue: LGY0.75/25-BL (http://www.tme.eu/en/details/lgy0.75_25-bl/single-core-cable-strand/bq-cable/)
Farnell | Brown: 2528103, (http://export.farnell.com/pro-power/pp001205/tri-rated-wire-0-75mm2-brown-1m/dp/2528103) Blue: 2528092 (http://export.farnell.com/pro-power/pp001196/tri-rated-wire-0-75mm2-blue-1m/dp/2528092)
| | Connectors
Side A | AUX PS module (X3) | Side B | Lower AC/DC module power input
Housing type | See Side B, Section C | Housing type Female quick disconnect
TME | - | TME | BM01148 (http://www.tme.eu/en/details/bm01148/non-insulated-terminals/bm-group/bm-01148/) or ST-003/2 (http://www.tme.eu/en/details/st-003_2/non-insulated-terminals/ninigi/)
Farnell | - | Farnell | 3625424 (http://export.farnell.com/jst-japan-solderless-terminals/sto-1-0t-187n-8/terminal-female-4-8x0-8mm/dp/3625424)
Pin | Female | Quantity | 2
Pin quantity | 2
TME | MX-5556-T3L (http://www.tme.eu/en/details/mx-5556-t3l/raster-signal-connectors-420mm/molex/039000078-39-00-0078-5556t3l/)
Farnell | 9732675 (http://export.farnell.com/molex/39-00-0078/crimp-socket-16awg-pk100/dp/9732675)

Wiring:
Name | Position | Color / description | Position | Color / description
Neutral | 4 | Blue | N/A | Female quick disconnect
Line | 5 | Brown | N/A | Female quick disconnect

### 7. Pre-assembled cables

### 7.1. Arduino shield power cable

Length | 300 mm
Type | Ribbon cable with IDC connectors; 10x28AWG
TME | FC10300-0 (http://www.tme.eu/en/details/fc10300-0/ribbon-cables-with-idc-connectors/amphenol/)
Farnell | N/A


Picture

Pinout:

Name | Position | Description
Gnd | 1 | Ground
Gnd | 2 | Ground
PWR_DIRECT | 3 | Triac control (continuous power)
PWR_SSTART | 4 | Triac control (soft-start)
FAN_SENSE | 5 | Tachometer output
FAN_PWM | 6 | Fan PWM speed control
DOUT2 | 7 | Power relay control
+5V | 8 | +5 V for Arduino Shield
Gnd | 9 | Ground
+5V | 10 | +5 V for Arduino Shield

### 7.2. Arduino USB cable

Length | 300 or 500 mm
Type | USB Micro to 5-pin receptacle cable
TME | N/A
Farnell | N/A
AliExpress | e.g. High Quality 50CM micro usb 5pin male to 1x 5Pin Female 0.1" USB header PCB motherboard cable (https://www.aliexpress.com/item/Free-Shipping-50CM-micro-usb-5pin-male-to-1x-5Pin-Female-0-1-USB-header-PCB/32233605468.html)

Pinout:


Name | Position | Color | Description
VCC | 1 | Red | +5 Vdc
D- | 2 | White | Data -
D+ | 3 | Green | Data +
GND | 4 | Black | Ground
Shield | 5 | Black | Shield

### 8. BOM

Type | Part (Farnell) | Part (TME) | Total
Receptacle | 865667 (http://export.farnell.com/harwin/m20-1060800/crimp-housing-8way/dp/865667) | NSR-08 (http://www.tme.eu/en/details/nsr-08/pin-headers/ninigi/) | 2
Receptacle | 143127 (http://export.farnell.com/molex/22-01-2035/crimp-housing-2-54mm-3way/dp/143127) | MX-6471-031 (http://www.tme.eu/en/details/mx-6471-031/raster-signal-connectors-254mm/molex/022012035-22-01-2035-6471-03i/) | 1
Receptacle | 143126 (http://export.farnell.com/molex/22-01-2025/crimp-housing-2-54mm-2way/dp/143126) | MX-6471-021 (http://www.tme.eu/en/details/mx-6471-021/raster-signal-connectors-254mm/molex/022012025-22-01-2025-6471-02i/) | 1
Receptacle Mini-Fit Jr. | 9963480 (http://export.farnell.com/molex/39-01-4030/crimp-housing-rcpt-sil-3way-mini/dp/9963480) | MX-5557-03R2 (http://www.tme.eu/en/details/mx-5557-03r2/raster-signal-connectors-420mm/molex/039014030-39-01-4030-5557-03r2/) | 2
Receptacle Mini-Fit Jr. | 9963502 (http://export.farnell.com/molex/39014050/crimp-housing-rcpt-sil-5way-mini/dp/9963502) | MX-5557-05R2 (http://www.tme.eu/en/details/mx-5557-05r2/raster-signal-connectors-420mm/molex/039014050-39-01-4050-5557-05r2/) | 1
Pin | 1022219 (http://export.farnell.com/harwin/m20-1180042/crimp-socket-gold-22-30awg-pk100/dp/1022219) | NDR-T (http://www.tme.eu/en/details/ndr-t/pin-headers/ninigi/) | 15
Polarising key | 512023 (http://export.farnell.com/harwin/m20-003/polarising-key-pk100/dp/512023) | NSDR-KEY (http://www.tme.eu/en/details/nsdr-key/pin-headers/ninigi/) | 1
Pin | 2063734 (http://export.farnell.com/molex/08-50-0113/contact-crimp-terminal-30-22awg/dp/2063734) | MX-0850-0114 (http://www.tme.eu/en/details/mx-0850-0114/raster-signal-connectors-254mm/molex/008500114-08-50-0114-2759-p909l/) | 5
Pin | 9732675 (http://export.farnell.com/molex/39-00-0078/crimp-socket-16awg-pk100/dp/9732675) | MX-5556-T3L (http://www.tme.eu/en/details/mx-5556-t3l/raster-signal-connectors-420mm/molex/039000078-39-00-0078-5556t3l/) | 11
Female quick disconnect | 3625424 (http://export.farnell.com/jst-japan-solderless-terminals/sto-1-0t-187n-8/terminal-female-4-8x0-8mm/dp/3625424) | BM01148 (http://www.tme.eu/en/details/bm01148/non-insulated-terminals/bm-group/bm-01148/) or ST-003/2 (http://www.tme.eu/en/details/st-003_2/non-insulated-terminals/ninigi/) | 6

Ferrule | 841195 (http://export.farnell.com/weidmuller/h0-75-14/ferrule-insulated-0-75mm-white/dp/841195) | H0.75/14D/GY (http://www.tme.eu/en/details/h0.75_14d_gy/bootlace-ferrules/weidmuller/9019040000-h07514d-gr/) | 6
Ferrule, twin entry | 1121751 (http://export.farnell.com/weidmuller/9037410000/ferrule-twin-entry-0-75mm/dp/1121751) | H0.75/15D2/GY (http://www.tme.eu/en/details/h0.75_15d2_gy/bootlace-ferrules/weidmuller/9037410000-h07514d-zh-gr/) | 5
Ring terminal | 7356528 (http://export.farnell.com/jst-japan-solderless-terminals/lrb-1-0t-m3/crimp-terminal-ring-m3/dp/7356528) | BM 91103 (http://www.tme.eu/en/details/bm91103/non-insulated-terminals/bm-group/bm-91103/) | 1
Cat5e cable | 1602385 (http://export.farnell.com/draka/900221va0000fe0100/cable-patch-5e-utp-grey-100m/dp/1602385) | HELUKAT100-FTP-FP (http://www.tme.eu/en/details/helukat100-ftp-fp/telecommunication-cables/helukabel/80055/) | 0.25 m
0.75 cm² cable (Brown) | 2528103 (http://export.farnell.com/pro-power/pp001205/tri-rated-wire-0-75mm2-brown-1m/dp/2528103) | LGY0.75/25-BR (http://www.tme.eu/en/details/lgy0.75_25-br/single-core-cable-strand/bq-cable/) | 0.43 m
0.75 cm² cable (Blue) | 2528092 (http://export.farnell.com/pro-power/pp001196/tri-rated-wire-0-75mm2-blue-1m/dp/2528092) | LGY0.75/25-BL (http://www.tme.eu/en/details/lgy0.75_25-bl/single-core-cable-strand/bq-cable/) | 0.43 m
0.75 cm² cable (Red) | 2528175 (http://export.farnell.com/pro-power/pp001270/tri-rated-wire-0-75mm2-red-1m/dp/2528175) | LGY0.75/25-RD (http://www.tme.eu/en/details/lgy0.75_25-rd/single-core-cable-strand/bq-cable/) | 0.75 m
0.75 cm² cable (Black) | 2528082 (http://export.farnell.com/pro-power/pp001186/tri-rated-wire-0-75mm2-black-1m/dp/2528082) | LGY0.75/25-BK (http://www.tme.eu/en/details/lgy0.75_25-bk/single-core-cable-strand/bq-cable/) | 0.75 m
0.75 cm² cable (Yellow-Green) | 2528140 (http://export.farnell.com/pro-power/pp001239/tri-rated-wire-0-75mm2-grn-yellow/dp/2528140) | LGY0.75/25-YL/GR (http://www.tme.eu/en/details/lgy0.75_25-yl_gr/single-core-cable-strand/bq-cable/) | 1.61 m
0.35 cm² cable | 2425402 (http://export.farnell.com/pro-power/mc6a-7-0-2t2-bn-100/equipment-wire-0-22mm2-brown-per/dp/2425402) | LGY0.35/25-BR (http://www.tme.eu/en/details/lgy0.35_25-br/single-core-cable-strand/bq-cable/) | 0.29 m
12 Vdc cooling fan | – | MB60251V1-G99 (http://www.tme.eu/en/details/mb60251v1-g99/dc12v-fans/sunon/mb60251v1-000u-g99/) | 1
NTC | 1187031 (http://export.farnell.com/vishay/ntcle100e3103jb0/thermistor-10k-5-ntc-rad/dp/1187031) | NTCLE100E3103JB0 (http://www.tme.eu/en/details/ntcle100e3103jb0/tht-measurement-ntc-thermistors/vishay/) | 1
IDC ribbon cable | – | FC10300-0 (http://www.tme.eu/en/details/fc10300-0/ribbon-cables-with-idc-connectors/amphenol/) | 0.3 m
USB Micro cable | Shenzhen Wonderwing Electronics Ltd. (https://wonderwing.en.alibaba.com/) or search e.g. Aliexpress | | 0.5 m

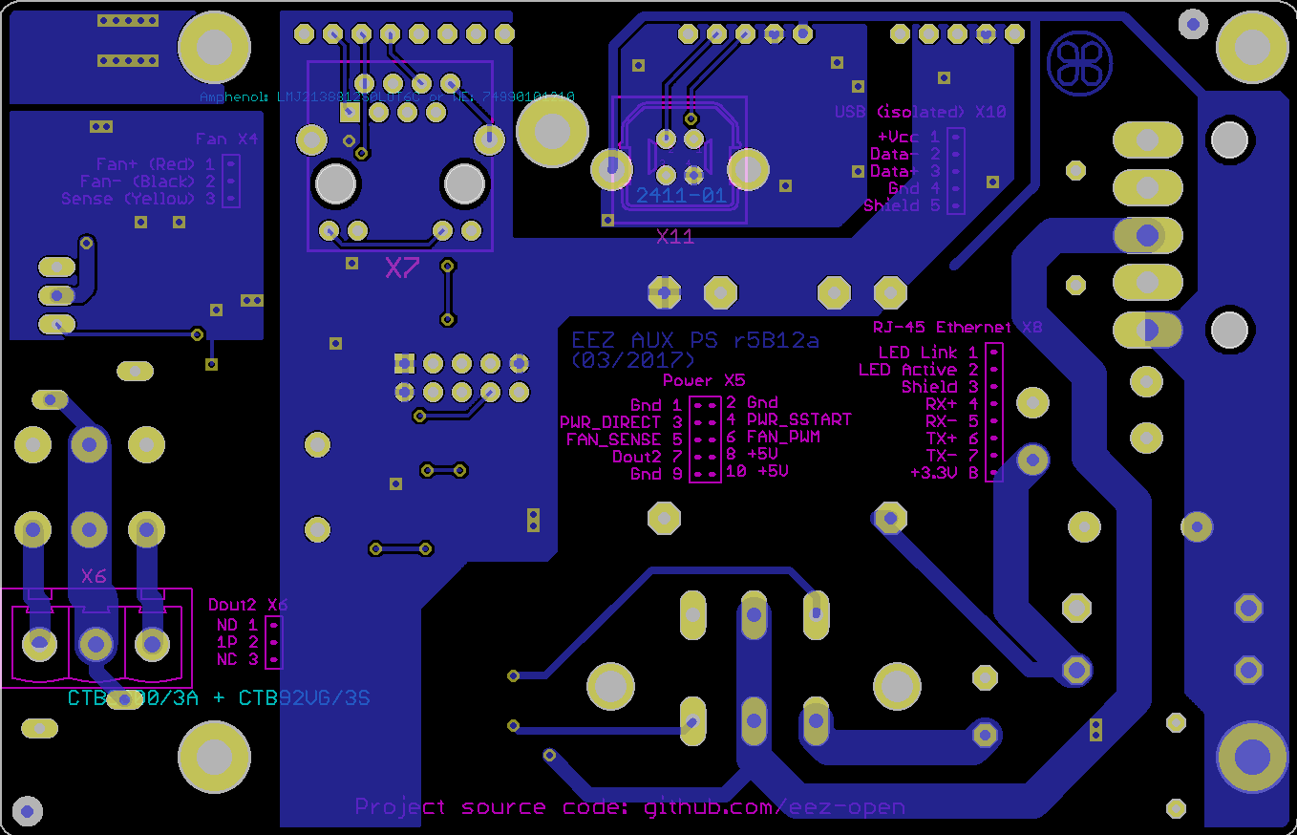
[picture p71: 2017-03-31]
Building instructions/AUX PS r5B12a assembly (bottom layer).png

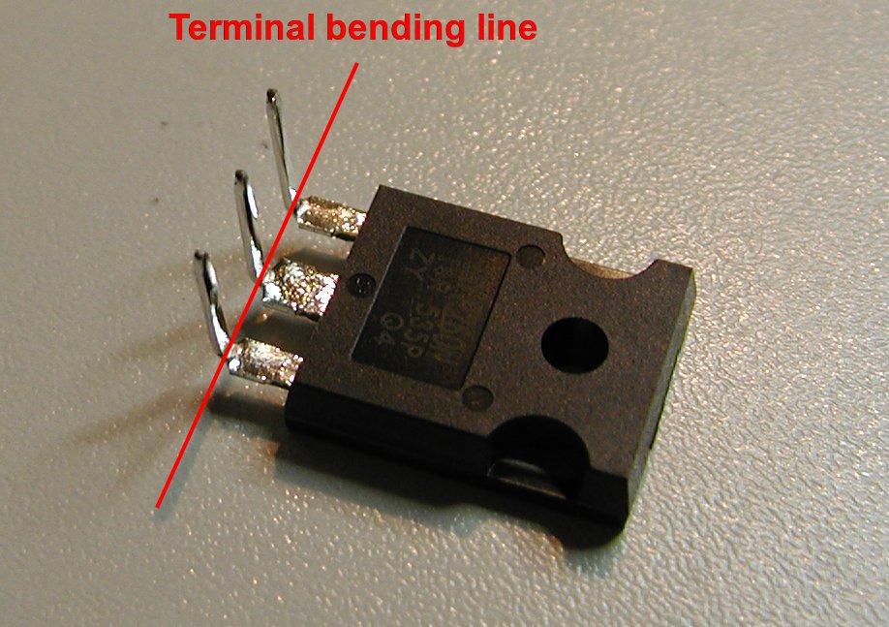
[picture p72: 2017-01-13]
Building instructions/Power board Q4 pins bending.JPG

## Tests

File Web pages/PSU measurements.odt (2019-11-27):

# Measurements

Table of contents

- Load transient response testing using MOSFET switch
- Load transient response testing using closed loop load transient tester
- Short circuit recovery
- Capacitive load
- Inductive load
- Output voltage programming (internal)
- Output voltage programming (external)
- Output enable programming
- Change the mode of operation (CV/CC)
- Power on, stand-by and forced power off
- Power on with shorted output

## Load transient response testing using MOSFET switch

The simplest way to measure load transient response is to use a MOSFET as a fast switch that will connect an additional load in parallel, increasing output current. The MOSFET switch (Fig. 1) is driven with signal generator (blue trace on Fig. 2). Output voltage will be set to 12 V. A permanently connected load of 8.2 Ω, and the MOSFET switch repetitively connecting an additional 33 Ω load will test the transient behavior of the PSU. The output current will alternate between 1.46 A and 1.83 A. The output voltage is shown on the scope image in cyan trace and the voltage on the MOSFET input in magenta. A larger difference between two currents will generate a larger output voltage disturbance; in this case it is -42 mV (or 0.35 % of output voltage) when the additional load is applied (rising edge) and -46 mV (0.38 %) when that load is disconnected (falling edge). The recovery time is marked by two vertical cursor lines and it is about 250 μs.

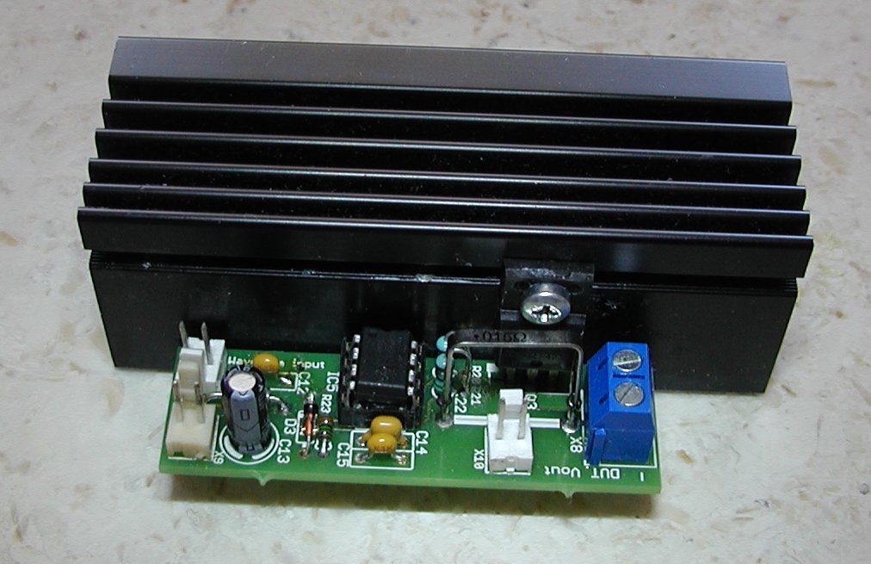
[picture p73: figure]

(http://www.envox.hr/eez/images/mosfet_switch.jpg)Fig. 1: Driver for MOSFET switch

## Load transient response testing using a closed loop load transient tester

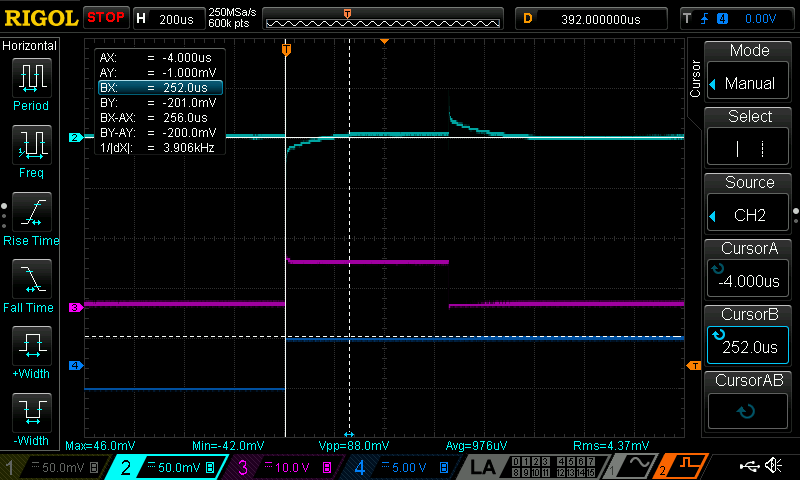
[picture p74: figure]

(http://www.envox.hr/eez/images/load_trans_res_with_mosfet.png)Fig. 2: Load transient response tested with MOSFET as a switch

The load transient response could also be tested using the circuit that is presented in LTC’s AN104 (http://www.linear.com/docs/29876) application note. The theory of operation is described in detail there. The schematic shown on page 15 (Fig. D1) was built and the resulting PCB circuit installed in a diecast aluminum alloy box (Hammond 1590U (http://www.hammondmfg.com/dwg.htm)) together with two transformers for a bias supply of +/-15 V (Fig. 3). The Eagle, Gerber, files, as well as the BOM for this tester is available on the GitHub (https://github.com/eez-open/ltc-an104-transient-tester).

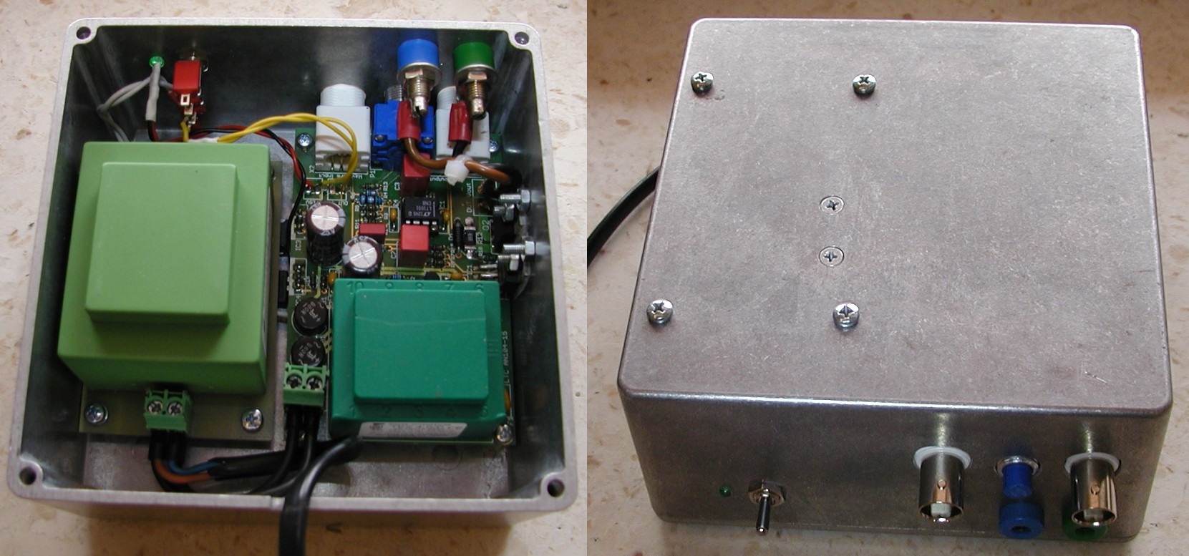
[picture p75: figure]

(http://www.envox.hr/eez/images/ltc_transient_tester.jpg)Fig. 3: Closed loop load transient tester

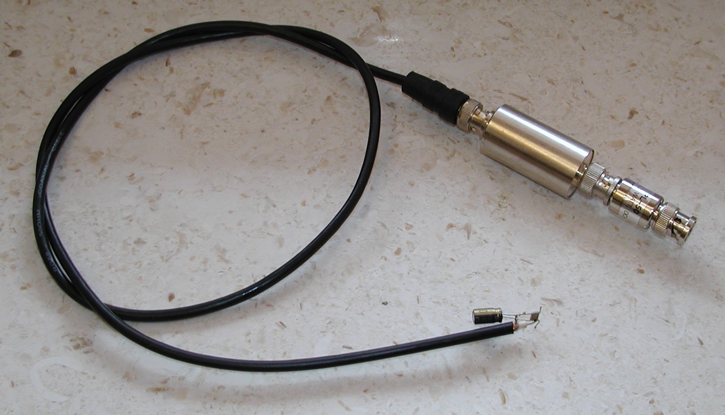
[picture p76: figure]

(http://www.envox.hr/eez/images/ac_probe_with_capacitors.jpg)Fig. 4: x1 AC probe used for measurements

The voltage measurement is AC coupled through home-made probe based on the recommendation the LT application note (pg 14, Fig C1). It used 4.7 μF instead of 10 μF, and at the cable tip an additional 10 μF electrolytic in parallel with a 470 nF ceramic capacitor.

(http://www.envox.hr/eez/images/ac_probe_on_ltc_tester.jpg)Fig. 5: AC probe connection on tester's input terminals

Measurements are conducted on the input terminals of the tester as shown on Fig. 5. The power supply output is set to 20 V with current set to the maximum value to avoid entering CC mode.

The result is shown on Fig. 6, 7 and 8, and was generated with a 1 Vpp signal (4 kHz, 20 % duty cycle) which corresponds to a 1 A change on top of a continuous load (the DC bias) of 1 A.

Warning: this tester should be used with special precautions if the programmed output voltage of the power supply is higher then 25 V. That could instantly damage the D44H11 switching transistor. The reason is that these conditions exceed the device's SOA (https://en.wikipedia.org/wiki/Safe_operating_area) (safe operating area) because it can accept only about 600 mA when Vce is 30 V. Consult the device's data sheet for more details.

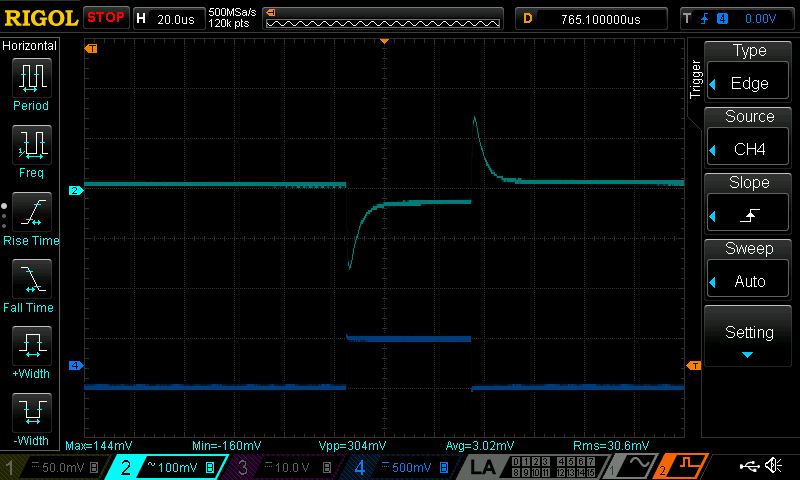
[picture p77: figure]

(http://www.envox.hr/eez/images/transient_response_ltc_tester.png)Fig. 6: Transient response with closed-loop tester

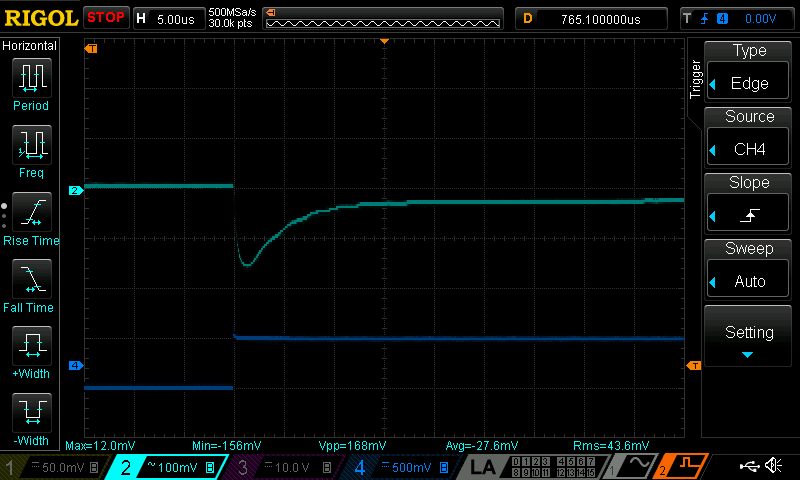
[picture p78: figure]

(http://www.envox.hr/eez/images/transient_response_ltc_tester_rising.png)Fig. 7: Transient response with closed-loop tester (rising edge)

## Short circuit recovery

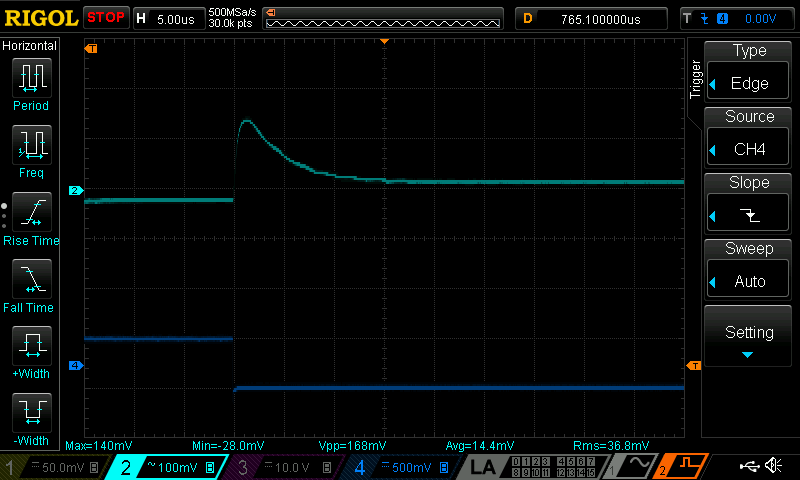
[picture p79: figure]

(http://www.envox.hr/eez/images/transient_response_ltc_tester_falling.png)Fig. 8: Transient response with closed-loop tester (falling edge)

Testing short circuit can be done using the MOSFET switch (Fig. 1) directly connected to the power supply’s output terminals. The output voltage is set to its maximum – for tested model that is 40 V. The output current is also set to a maximum value of 5 A. On Fig. 9, the cyan trace is the output voltage, the magenta trace the MOSFET gate signal derived from the input signal coming from the signal generator (blue trace). Recovery from a shorted output lasts about 1.7 ms.

## Capacitive load

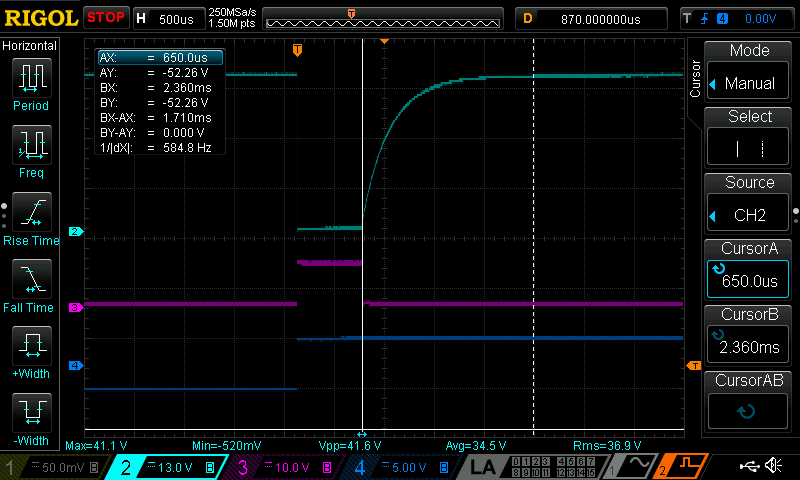
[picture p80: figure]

(http://www.envox.hr/eez/images/short_circuit_recovery.png)Fig. 9: Short circuit recovery

The capacitive load testing is performed by simply connecting a capacitor to the output terminals with oscilloscope probe already connected, A huge output voltage drop is expected from an uncharged capacitor. Fig. 10 shows what happened when the output voltage is set to 40 V and a 10 000 μF electrolytic is connected. Note the capacitor is polarized and must be connected correctly.

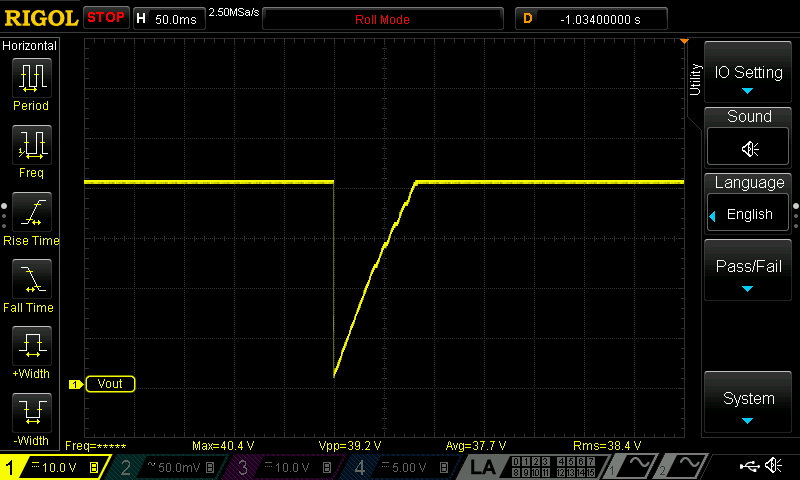
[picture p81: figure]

(http://www.envox.hr/eez/images/capacitive_load_10mf.png)Fig. 10: Output voltage drop when a large uncharged capacitor is connected

Another scenario was to leave a capacitor connected and program output using the OE signal. The DP (down-programmer) circuit was left active so the charged capacitor can be discharged before the output is enabled again.

## Inductive load

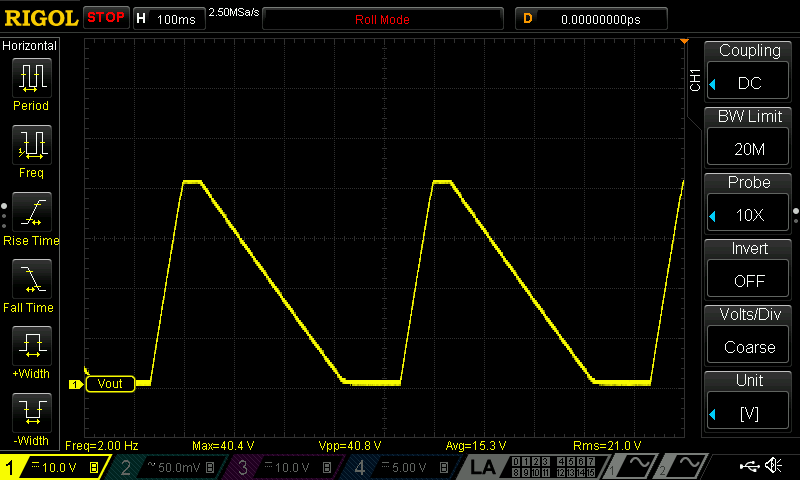
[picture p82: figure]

(http://www.envox.hr/eez/images/capactive_load_2200uf_oe.png)Fig. 11: Output controlled with OE signal and 2200 μF capacitive load

We tested two types of inductive load, a RS540 type DC motor and a 100 μH power inductor (Bourns 2312V series). The DC motor was connected directly and bypassed with additional 100 μF electrolytic capacitor. It generated many spikes, but there was no visible oscillation.


(http://www.envox.hr/eez/images/dc_load_5ms.png)Fig. 12: Output voltage with DC motor connected (timebase 5 ms)


(http://www.envox.hr/eez/images/dc_load_500us.png)Fig. 13: Output voltage with DC motor connected (timebase 0.5 ms)

The power inductor was not continuously connected to the output. A MOSFET switcher (Fig. 1), driven with a 100 Hz signal was used (the yellow trace is the output voltage, the magenta is the MOSFET gate signal, and the blue is the signal generator output).

(http://www.envox.hr/eez/images/inductive_load_40v_1a.png)Fig. 14: Inductive load testing (Vout=40 V, Iout=1 A)

## Output voltage programming (internal DAC)


(http://www.envox.hr/eez/images/inductive_load_5v_2a5.png)Fig. 15: Inductive load testing (Vout=5 V, Iout=2.5 A)

Testing the output voltage programming can demonstrate undesirable overshoots (https://en.wikipedia.org/wiki/Overshoot_(signal)) or undershoots when the output voltage is changed from a lower to a higher value, and vice versa. This test also shows the rise (up-programming) and fall (down-programming) times. The result shown in Fig. 16 was generated by changing the output voltage on a 40 V model from 2.5 V (the DAC code is 0x1000) to 10 V (DAC code 0x4000) and back to 2.5 V with no load connected.

## Output voltage programming (external)


(http://www.envox.hr/eez/images/vout_programming.png)Fig. 16: Output voltage programming (internal)

One of the power channel’s voltage outputs can be also programmed from an external source using the protected input accessible via the front panel connector located on the Arduino Shield. As in the case of internal programming, +2.5 V is required for full scale. In this operating mode it is possible to measure the maximum settling time because the input analog control signal is applied directly to the CV control loop.

If the programming input is 1.25 V, the output voltage will be set to +20 V (on the tested model) and the difference between the rising edges is the settling time – It is 120 μs as shown in Fig.17 with no load connected. Fig. 18 shows the output with a load connected. External programming can also show the benefit of the down programmer circuit.

With no load, the PSU requires 460 μs to reach zero from half scale.


(http://www.envox.hr/eez/images/vout_prog_ext_noload.png)Fig. 17: Output voltage programming from external source (1.25 V, 100 Hz), no load connected

## Change the mode of operation (CV/CC)


(http://www.envox.hr/eez/images/vout_prog_ext_load.png)Fig. 18: Output voltage programming from external source (1.25 V, 100 Hz), load 16.4 Ω

The PSU changes its operational mode when a particular programmed output value is reached. For example, if output current is set to 100 mA, the output voltage (already set to 20 V) will remain unchanged as long as the connected load does not sink more then maximum, current allowed; therefore, its resistance must be equal to or greater than 200 Ω. A sudden change in resistance that could change a mode of operation must be “smooth” – no oscillation nor overshooting are permitted during a transition. This test was performed by repetitively connecting and disconnecting a 33 Ω load with a MOSFET switch (Fig. 1) driven by 10 Hz from the signal generator. The output voltage was set to 40 V (the maximum allowed by the model being tested) and current limited to 250 mA. Therefore when the right load is applied, the PSU should change mode from CV to CC which will cause the output voltage to drop to ~8 V.

## Output enable programming


(http://www.envox.hr/eez/images/cc_cv_testing.png)Fig. 19: Mode of operation changes

Output enable programming should have the same effect as output voltage programming from a value greater then zero, to zero volts, using the DAC. But since output enable is a different circuit it must be tested separately to test its overshooting and undershooting characteristics. Two cases were tested with no load, changing the output state with the voltage set to 2.5 V (Fig. 20), and then with the voltage set to the maximum (for the tested model) of 40 V (Fig. 21). A difference in fall time (down-programming) is clearly visible (<260 μs versus 1.78 ms).


(http://www.envox.hr/eez/images/output_enable_2v5.png)Fig. 20: Output enable testing (Vout=2.5 V)

## Power on, stand-by, and forced power off


(http://www.envox.hr/eez/images/output_enable_40v.png)Fig. 21: Output enable testing (Vout=40 V)

When the power supply is powered on, the output voltage should show no signs of overshoot. In principle, this is the same issue as discussed above – output enable programming followed by output voltage programming. The moment when the power supply channel's output reaches its programmed value after being powered on is shown on Fig. 22. A well defined transition from no voltage to the set voltage should not be a surprise since powering-on is under control of the MCU firmware, is adjusted long enough after all pre-regulator and post-regulator circuits are stabilized to cause little trouble.


(http://www.envox.hr/eez/images/power_on_vout_30v.png)Fig. 22: Power on with output voltage set to 30 V

(http://www.envox.hr/eez/images/power_off_no_load.png)Fig. 23: Power off (AC mains unplugged, Vout=30 V, no load)

Fig. 23 and 24 show what happens when the AC mains is abruptly unplugged without, and with, a load connected (100 Ω in this case). Therefore no MCU assistance is possible, but no surprises were detected. It's also true with a very low output voltage set (i.e. below the operational amplifiers bias voltage of 5 V). Fig. 25 shows the state of the output at 3 V and with no load connected.

Fig. 26 shows output when the power off is MCU assisted. It is very similar to entering the standby mode.


(http://www.envox.hr/eez/images/power_off_with_load.png)Fig. 24: Power off (AC main unplugged) with 100 Ω load connected


(http://www.envox.hr/eez/images/power_off_no_load_3v.png)Fig. 25: Power off (AC mains unplugged, Vout=3 V, no load)

## Power on with shorted output


(http://www.envox.hr/eez/images/entering_stand_by.png)Fig. 26: Entering the stand-by mode (under MCU control)

Finally we want to know what will happen at power-up, when both voltage and current are programmed to the maximum level (40 V, 5 A for the model tested here ), and with the output terminals shorted (i.e. with a maximum output demand). Fig. 27 shows the PSU safely enters such mode of operation, and only small peak lasting less then 10 μs can be seen at the output.


(http://www.envox.hr/eez/images/power_on_shorted.png)Fig. 27: Power on with shorted output

Revision: 0.2 1 (of 14) Last modified: 2017-05-08

Last modified: 2017-05-08 12 (of 14) Doc. version: 0.2

Revision: 0.2 13 (of 14) Last modified: 2017-05-08

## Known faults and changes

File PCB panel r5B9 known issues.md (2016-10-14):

**Arduino Shield r3B4**
- Marking on bottom silkscreen for all red LEDs (LED_SP, LED_PROG1, LED_PROG2, LED_CC1, LED_CC2) is wrong (cathode and anode are swapped on HSMH-C170)
- X18 has to be right angled since it is positioned too close to the CH1 heatsink

**AUX PS r5B9**
- Side 2 of USB isolator (IC19) has no power connected. Add wiring from X10-1 to pin 16 and X10-4 to pin 9 if you'd like to add USB isolation.

**Power module r5B9**
- Voltage programming switch (IC13) is not wired correctly. Therefore remote programming cannot be selected without simple PCB correction (see *rprog_correction.jpg* in Building instructions folder).
- The main (Q4) heatisink is earthed, cut that PCB trace to decrease EMI (see *heatsink_earth.jpg* in Building instructions folder).

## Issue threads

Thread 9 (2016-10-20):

eez-open/psu-hw #9: Fan generates EMI

prasimix, 2016-10-20:
When cooling fan is active, and additional noise could be measured on the channel's output. We need here better filtering or maybe switching from PWM to linear speed control could improve situation.

PurnenduK90, 2017-01-30:
Can you point out which board is having the fan controller and where is it mounted. As I work on KiCAD/Allegro hence can't open your design files. If you can point out PDF or image may be I can help.

prasimix, 2017-01-30:
It's located on AUX PS module, you can find it on [Sheet 7of11](https://raw.githubusercontent.com/eez-open/psu-hw/master/Consolidated/EEZ%20PSU%20consolidated%20r5B11%20Sheet%207of11.png). Q22 is driven with MCU PWM signal `AUX_FAN_CTRL`.

PurnenduK90, 2017-01-30:
Sorry, I meant PCB implementation, is it properly shielded from the main board. As I don't have the complete picture hence I can only guess. Please look into following points:

1. What is the frequency of noise in main power {Is this same or some multiplier of fan controller switching frequency.}, If yes, you can do following things;

- Provide an isolated ground (1uh inductor)
-Provide an isolated power with sufficient input capacitors
-Make sure switching lines are separated by output traces by ground plane of 3*trace width and followed by ground vias separated maximum by 1/20th of the switching frequency wavelength.
-Heating also cause the rise in noise so please make sure MOSFET is not heating up.
-Physical position of fan can also be the reason of noise due to rotating field (minor)
-For simplicity, a linear controller can also be used.

if the noise frequency is different than fan switching or its harmonics, it means some noise is finding return path through fan circuit. In this case, the above-mentioned steps will still help.

prasimix, 2017-01-30:
Thanks for that. The physical location of both AUX PS module and fan can be see on [picture1](http://www.envox.hr/eez/images/galleries/psu-h24005/02_PSU_H24005_topview_open.JPG) and [picture2](http://www.envox.hr/eez/images/galleries/psu-h24005/07_fan_orientation.JPG) (both of them are mounted directly on the enclosure's rear panel). PCB layout is shown below (fan section is in down right corner as marked with green rectangle):

[image]

[image]

[image]

Fan PWM signal is 1 kHz, while main switcher is on 320 kHz.
I'm thinking to replace existing AC/DC 12V PCB converter (TR2) that is used for powering Arduino shield (using step down IC16, see [Sheet 6of11](https://raw.githubusercontent.com/eez-open/psu-hw/master/Consolidated/EEZ%20PSU%20consolidated%20r5B11%20Sheet%206of11.png)) with one that has two isolated outputs: +5V and +12V. In that case fan could be powered separately and PWM signal can be isolated with adding an opto-coupler. Maybe that is a right approach even if linear controller is used.

prasimix, 2017-01-31:
This is a new proposal for fan driver with isolated power supply. It's based on Vigortronix VTX-214-005-0512 dual isolated outputs power supply (+5V, +12V). Fan control and speed sense is accomplished using two opto couplers.

[image]

PurnenduK90, 2017-02-01:
I think OK5 is conducting more or equal to the maximum specified load current. I will suggest R128 to be replaced by 2.2K. 
I didn't find the spice model for SKL16, although, with another Schottky diode, I found circuit was not regulating properly with fan model I choose. If you can give some specification of fan model I can comment further. Also, fan-sense circuit is not very clear to me. Just curious, what is output of fan sense (a constant voltage based on fan speed/ PWM based on fan speed).

prasimix, 2017-02-01:
With existing R128 max. Ic on OK5 is limited below 6.5 mA. That is well below max. rating from HCPL-151 datasheet (30 mA @ If=5 mA). I also found that fan sense output max. Ic=4 mA therefore I added Q13 as on picture below. Fan is [SUNON MB60251V1-000U-G99](http://www.tme.eu/en/details/mb60251v1-g99/dc12v-fans/sunon/mb60251v1-000u-g99/).

[image]

PurnenduK90, 2017-02-01:
yes, you are correct I misread the exponent value. This circuit seems fine although I would like to increase the value of c97 to 10m to filter out the ripple. As fan speed control is not required instant task so I will not mind the soft change in voltage level.

prasimix, 2017-02-01:
Huh, 10m for C97 looks quite challenging on existing PCB :). I'll see what is the biggest possible package that can be included.

PurnenduK90, 2017-02-01:
what package is used in current board

prasimix, 2017-02-01:
Ø6.3 x 7.7mm

prasimix, 2017-02-13:
VTX-214-005-0512 is tested under full load on both rails and it works fine. I'll continue when new PCB arrive.

prasimix, 2017-03-14:
It seems that isolated fan power did the job.

closed 2017-03-14 by prasimix

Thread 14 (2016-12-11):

eez-open/psu-hw #14: Isolate TPS3705 reset signal

prasimix, 2016-12-11:
Arduino IDE cannot reset the board when firmware is uploaded and reset has to be applied after uploading attempt. The reason for that is that TPS3705 is holding RESET line high (inactive). That makes a whole uploading procedure longer (and frustrating). Add one diode to "isolate" TPS3705 reset pin from Ardino Due RESET line.

prasimix, 2016-12-11:
Fixed

closed 2016-12-11 by prasimix

algaremi, 2016-12-13:
Do you have a schematic for this mod? I would like to add it to my Arduino shield. Thanks
SB

prasimix, 2016-12-13:
This one is not trivial, it require that IC32 is removed that one trace beneath it can be cut. Also one 0.8 mm hole has to be drilled on the right position. Use any THT signal diode e.g. 1N4148:

[image]

[image]

[image]

bgat, 2016-12-13:
Why not just lift pin 7 on IC32?

prasimix, 2016-12-13:
Good point, thanks! :+1:

bgat, 2016-12-13:
Wait, nevermind... 😂

bgat, 2016-12-13:
Wait, I take that back...once you lift pin 7, and just looking at the pics (and not schematics, which I don't have in front of me), it appears you might have a couple of vias you could solder the diode to. So maybe the pass-thru hole isn't necessary.

I belabor the point only because drilling is irreversible, and if a noob (like me when I'm under caffeinated) makes that kind of mistake, suddenly they're into a much bigger problem...

prasimix, 2016-12-13:
I understand that. If you really want to be on the safe side, forgot this hack. Only obstacle is that you need to push reset manually while firmware is uploading.

bgat, 2016-12-13:
Nope, I want automatic AND safety. Call me lazy, or call me preparing for someone like me who won't read directions. 😂

prasimix, 2016-12-13:
:) that's also fine. That's why this issue is opened and fixed in the recent revision.

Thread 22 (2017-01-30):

eez-open/psu-hw #22: Suggestions

PurnenduK90, 2017-01-30:
After changing to subscription based licensing I think this project should move to KiCAD. It has a lot of potentials. I will also suggest some fixed outputs to easily work with digital design. e.g. 5V, 3.3V, 2.5V, 1.25V. As an electronics engineer, I never find one power supply enough for testing purpose, due to multiple voltage levels required in modern designs.

prasimix, 2017-01-30:
Please open one issue per suggestion in the future.

prasimix, 2017-01-30:
For multiple outputs we should in the future replace existing AC/DC converters (2 x 48V, 1 x 12V) with one **open source** LLC converter ([example](https://github.com/yu3ma/FSFR2100_LLC_SMPS)) with multiple isolated outputs. 
Another possibility is to go with "rackable" design with backplane that can grow to at least 8 different test&measurements modules with central TFT console.

prasimix, 2020-01-20:
For multiple outputs check [EEZ BB3](https://github.com/eez-open/modular-psu) project.

closed 2020-01-20 by prasimix

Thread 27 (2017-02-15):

### ISSUE TITLE
possible spike when switching sense relay

### ISSUE THREAD

**Issue by faultylee** [eez-open/psu-hw#27]
Hi guys, great job on the PSU design, and also making this open source. 

Btw, I noticed that there's could possibly be voltage spike when switching sense relay on and off. Also, when the remote sense input is disconnected accidentally or when the relay fail, how much will the output voltage be restricted?

**Comment by prasimix** [comment]
Thanks for your input. R32, R57 (see [Sheet 3 of 12](https://raw.githubusercontent.com/eez-open/psu-hw/master/Consolidated/EEZ%20PSU%20consolidated%20r5B12%20Sheet%203of12.png)) is a guard against entering remote sensing when remote sense inputs are not connected with the power outputs. 
Another guard is remote polarity detection accomplished with Q18, Q20 (see [Sheet 5 of 12](https://raw.githubusercontent.com/eez-open/psu-hw/master/Consolidated/EEZ%20PSU%20consolidated%20r5B12%20Sheet%205of12.png)) when wiring is wrong or insufficient (i.e. only one input is connected to the power output).

**Comment by faultylee** [comment]
:+1:

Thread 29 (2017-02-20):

### ISSUE TITLE
Where can I find the complete schematic diagrams?

### ISSUE THREAD

**Issue by dagema** [eez-open/psu-hw#29]
I have looked through all repositories, but am unable to find any detailed schematic diagrams. Does that not belong included in open HW design?  Where can I find it? I am not interested in BOM or board layouts, only the schematics.

**Comment by prasimix** [comment]
All schematic is available in three formats: [Eagle](https://github.com/eez-open/psu-hw/blob/master/Consolidated/Eagle%20files/EEZ%20PSU%20consolidated%20r5B12.sch), [bitmaps](https://github.com/eez-open/psu-hw/tree/master/Consolidated) and [pdf](https://github.com/eez-open/psu-hw/blob/master/Consolidated/EEZ%20PSU%20consolidated%20r5B12.pdf). Information about that can be find also on the "home page" ([README.md](https://github.com/eez-open/psu-hw/blob/master/README.md)) of this repository where you can read:

_Files in this repository are organized using the following folders:_
- _Consolidated - contains information about all modules. That include BOM with parts required to build complete dual channel unit (1 x Aux, 2 x Power, and 1 x Arduino Shield). Use this as a primary reference for PCB manufacturing and assembling._
- _Aux power - information about Auxiliary power module only_
- _Power board - information about Power board only_
- _Arduino shield - information about Arduino Shield only_
- _Mechanical - drawings for metal custom enclosure and acrylic demonstration enclosure._

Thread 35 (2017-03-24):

eez-open/psu-hw #35: BOM Errors?

jwilhelm1, 2017-03-24:
R18 on the power boards isn't listed in the BOM
The listed inductor for L1 doesn't fit the board footprint. RN114-4-02-1MS does fit.

prasimix, 2017-03-24:
R18 is missing, I'm going to add it, but I'm not so sure about L1. It's changed from 1.5mH to 0.7mH that is much smaller but both can be used (it's now smaller due to #25). Please let me know what Power board revision you are referring at?

jwilhelm1, 2017-03-24:
The power board I am assembling is 02/2017 r5B12.

prasimix, 2017-03-24:
OK, but r5B12 is still open for revisions and you can see that few builds exists on the GitHub (started from Feb 13th build d9b361a). That will be like that until it become an official new release that will be listed [here](https://github.com/eez-open/psu-hw/releases).  
It's quite possible that you used some of earlier builds and have the following situation:

[image]

jwilhelm1, 2017-03-24:
Thanks. I'm new to GitHub, so I'm still learning how to navigate it.

closed 2017-03-24 by jwilhelm1

prasimix, 2017-03-24:
No problem, and many thanks for your patience and contribution.

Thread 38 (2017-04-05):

### ISSUE TITLE
Pin numbering of L1 (RN112-4-02) is wrong. 

### ISSUE THREAD

**Issue by phuebner** [eez-open/psu-hw#38]
I noticed that the pin numbering of the choke L1 on the power board is not matching the datasheet.
[Datasheet RN112-4-02](http://www.schaffner.com/fileadmin/media/products/pim/DS_RNseries_20110616_web18.pdf)
<img src="https://cloud.githubusercontent.com/assets/4952144/24693309/2f13ab1e-19dd-11e7-8aa9-0372b9713afa.png" width="400">
<img src="https://cloud.githubusercontent.com/assets/4952144/24693327/4ab29d12-19dd-11e7-8081-75e5b91db32a.png" width="400">

**Comment by prasimix** [comment]
Fixed

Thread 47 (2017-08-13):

eez-open/psu-hw #47: Unit won't power on

madscientist159, 2017-08-13:
Received kit today, set both internal PSUs to 115V (local US voltage), assembled it, eagerly plugged it in and ... nothing.  No lights, no fan, nothing.

Double checked all wiring already; will start debugging shortly.  Has anyone else experience this?  Note that on my unit the rear power switch did not easily go into the "On" position; I don't know if I may have received a unit with a defective rear power switch?

madscientist159, 2017-08-13:
And in case anyone asks, yes, the fuse tray is installed with both fuses :wink:

madscientist159, 2017-08-13:
And the verdict is...defective mains switch :nauseated_face:   One pole doesn't close in the "On" position.

Can I just get a replacement switch sent out?

madscientist159, 2017-08-13:
Starting to wonder if you guys shipped a defective rear panel.  With mains switch bypassed unit enters boot loop; seems like main PSU can't supply enough power to keep front panel / control electronics engaged.  Unit tries to start up, runs out of stored energy in PSU caps, then resets and tries to start up again.

Not exactly a happy camper here. :-1:

madscientist159, 2017-08-13:
Uplugging fan fixed startup issues but...no fan means unit is unable to be installed on bench.  This rear panel assembly seems to be quite messed up; can you overnight a new one?

prasimix, 2017-08-13:
Hi, as mentioned in the _[kit assembly instructions](http://www.envox.hr/eez/bench-power-supply/group-buy-kit-assembly.html)_ PCB modules are tested independently of accompanying parts therefore AUX power module board is tested without all parts mounted on the rear panel. But, all parts are genuine and installed as received from the distributor (e.g. TME in case of main switch). It's possible that main switch is ruined while wires are inserted in it. But, that cannot explain why AUX power module doesn't work. Please first check without any load if you can get +5 V and +12 V on its outputs.

madscientist159, 2017-08-13:
Interesting that you mention that.  Just checked under load and the "12V" output reads 17V (!) while the 5V output is a stable 4.95V.

FWIW I am an electrical engineer with many, many years experience with systems that are more complex than this one.  The switch problem I can sort of understand, what I don't understand is how this unit passed testing with a faulty standby regulator module.

madscientist159, 2017-08-13:
@prasimix Any idea of when I can get a replacement for the failed module?  We have rework facilities here so if it will be faster to just send out a switch module and a replacement VTX-214-005-0512 I'm OK with that.

prasimix, 2017-08-13:
If I understand you correctly TR1 +12 V rail is defective. But, even if that is a case, with proper +5 V rail your unit should start and power up self-test will report fan error. Please let me know what you get in you case.

madscientist159, 2017-08-13:
@prasimix That is exactly what happens.  I don't want to run the unit w/o a fan since the two power supply boards contain linear regulators and I get concerned about overall heat dissipation.

prasimix, 2017-08-13:
Ok, overheating cannot happen since firmware when detecting fan error limit max. output current to 2 A (defined by `ERR_MAX_CURRENT` constant).

madscientist159, 2017-08-13:
@prasimix Good to know.  Still, I purchased a kit that was supposed to be fully functional and I need more than 2A on the outputs.  How soon can I get replacements for the two defective components?

prasimix, 2017-08-13:
I cannot answer in this moment how soon you can get replacement. Please note that we are not factory, and that this campaign was actually a group buy. Therefore no extra boards nor service parts are available. I have to order it, and that will take time. Also I cannot initiate a new order as someone report a problem, but I have to combine parts from more incidents (if that will happen) to save shipping costs.

madscientist159, 2017-08-13:
@prasimix All right then, how about a partial refund and I'll just source the parts?

prasimix, 2017-08-13:
That's also possible, I have to discuss that with Crowd Supply first. Give me a day or two.

madscientist159, 2017-08-13:
@prasimix OK, thanks! :smile:

prasimix, 2017-08-14:
Please send me your PayPal email using contact [form](http://www.envox.hr/eez/contact-us.html).

madscientist159, 2017-08-14:
@prasimix Email sent.

closed 2017-08-14 by prasimix

madscientist159, 2017-08-30:
Need to add one more defect to the list...this power board was a mess.  In addition to everything else (causing the module failure?) the fan power leads were swapped inside the fan connector!  Replacing the module and manually flipping the red / black wires appears to have restored the rear panel to operation, a couple of weeks late and with a $20 extra investment in replacement parts.

Overall not happy here...won't order again or recommend until the rear panel gets better QA.

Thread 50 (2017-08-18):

eez-open/psu-hw #50: EEZ H24005 Early Bird Kit Parts Shortage & Assy documentation errors

stolens, 2017-08-18:
EEZ H24005: Open Source Bench Power Supply Kit Early Bird Complete kit Parts Shortage.

There is a fulfillment shortage and documentation errors in the assembly manual for this kit.

Reference:
Complete kit EEZ H24005: Open Source Bench Power Supply
http://www.envox.hr/eez/bench-power-supply/group-buy-kit-assembly.html
A work in progress (Draft 0.7)

Parts group Bag#2, part B1. Parts list indicates only 2 pieces of M3x5 mm Black, Countersunk head screws when 4 are required causing a parts shortage in the kit. These are used in mounting the AC/DC Modules to the bottom enclosure. These are illustrated and described around Figures 16 and 17 in the assembly instructions.

Recommended corrective actions:
1. Provide 2 more of part B1 in the kit.
2. Correct the assembly instructions to indicate 4 pcs instead of 2 pcs in bag#2, the mounting hardware for the power modules. The assembly instructions are correct, the provided hardware and the parts list are deficient.

Crowd Supply recommended I post this as an issue.

prasimix, 2017-08-18:
Due to logistic issues we cannot organize sending of two additional screws. Sorry for that.  
But as you can see the main mean of fixing and securing AC/DC modules are mounting frame (B3) _not_ 40 mm spacers (B2). Therefore you can left lower side of spacers unfixed, or if you really want to do that you have a great freedom to chose some other M3 screws (length could be up to 30 mm!).

Kit assembly instructions document with this note is now also available [here](http://www.envox.hr/eez/bench-power-supply/group-buy-kit-assembly.html).

szwesleyzhao, 2017-08-19:
Cool, do you need turnkey pcb assembly service in china ? We could one stop stop service from prototype to mass production. Here is email; szhwpcba@gmail.com

davidcarne, 2017-08-26:
Regarding securing the spacers - I suggest against leaving one of the spacers secured with only the top screw. The spacer near the regulator module is not captive as the meanwell module doesn't have a full hole; only a notch. If the module is shaken or the screw/standoff connection isn't quite tight enough, it might shake loose leaving the standoff and screw loose in the enclosure. (This happened during my final assembly).

closed 2018-01-17 by prasimix

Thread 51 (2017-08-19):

### ISSUE TITLE
Power board self-test fail on newly assembled H24005

### ISSUE THREAD

**Issue by amuir2k** [eez-open/psu-hw#51]
Folks,

I just built up my fulfillment kit for the H24005, very well designed and executed - unfortunately - I'm getting a self-test error that IOEXP and ADC are failing on both channels.  I've updated to the latest FW, but this did not help.  All cables appear in good shape and in correct orientation.

Where to start to troubleshoot this?

Thanks,

Art

**Comment by prasimix** [comment]
1. Check if Power board have +48 V on its input (X1)
2. Check bias voltages on ferrite beads FB1 (+5 V), FB2 (+5 V) and FB3 (-5 V)

**Comment by amuir2k** [comment]
Thanks, that solved it, I hadn't switched the supplies off of the 230V
input setting (Doh!)

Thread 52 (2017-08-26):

eez-open/psu-hw #52: Difficult or unable to attach power modules to case...

mloftis, 2017-08-26:
On my unit the front panel PCB is bowed out slightly making the screw holes for the heatsinks not line up.  Looks to be about a ~1mm difference between the left (screen) side and right (output jacks).  The mounting plate for the screen also barely matches up with the screw holes on the bottom/through the case.

mloftis, 2017-08-26:
This appears to be due to too much overall length created by the jacks themselves.  It's JUST barely enough that the holes miss on the bottom of the case.

prasimix, 2017-08-26:
Please provide picture and mark questionable section.

prasimix, 2017-08-26:
Please also consider reply [#732](http://www.eevblog.com/forum/projects/diy-programmable-dual-channel-bench-psu-0-50v3a/msg1288779/#msg1288779) on the EEVblog forum.

mloftis, 2017-08-27:
Lighting in my office is terrible so it's really hard to see the bottom of case picture.  The screw holes just barely peek through the case holes no matter how you wiggle/maneuver the PSU modules if the front panel is secured.  But the top picture of the front panel alignment issue seems pretty obvious even in the pictures.  That's what's causing the misalignment of the PSU board heat sinks.  I was able to get it to assemble by very loosely attaching the front panel and then attaching the PSUs - I didn't see your post about the EEVblog post until after I'd attempted that way but that's exactly the workaround they came up with too.

[image]
[image]

prasimix, 2017-08-27:
OK, did you still have a problem or not? Does very loosely attaching the front panel before Power boards are mounted on bottom plate resolve this issue?

mloftis, 2017-08-28:
Yes, loosely attaching the front panel in order to gain the ~1mm movement to get the holes aligned worked.

closed 2017-08-28 by mloftis

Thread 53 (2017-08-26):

eez-open/psu-hw #53: issue with USB port

jlegen, 2017-08-26:
Hi,
i successfully assembled my psu device, values (without load and calibaration) are basically bang-on.
The only thing which i don't get working is the USB connector. Native port is only recognized as "device not started, Code 10" in device manager.
I tried several cables, and also checked that the internal cable is ok, and it's wired correctly.
I managed to update to firmware 1.01 by plugging a USB cable into DUE's native port directly, which means port and windows (driver) are ok.
I first thought it could only be a simple mechanical issue, but then i realized that it's got an isolator before the USB port... 8-}
Any ideas on that?

Update: is just tried to re-wire to DUE's programming port - and this works! I've been able to re-flash the firmware configured to prog-port as well, so at least it works "some how". 
Though the constant resetting of the whole thing is really annoying (played a bit with SCPI)...

Jan

prasimix, 2017-08-26:
Ok, so what is your problem here? Does USB isolator and provided USB patch cable (5-pin 0.1" to micro-USB) works with _programming_ but not with _native_ port on Arduino Due?

jlegen, 2017-08-26:
Yes. 
It just took me a while until i came to the idea to try the prog port, instead of native.

jlegen, 2017-08-26:
little FUP on this - according to USB-Tool, the native port's ID is read correctly, error happens afterwards; perhaps some out-of-spec passive at the Adum, resulting in some form of edge/corner case? 

Device Description       : USB-Verbundgerät
Device Path              : \\.\USB#VID_2341&PID_003E#5&1c6e4acc&1&1#{a5dcbf10-6530-11d2-901f-00c04fb951ed}
Device ID                : USB\VID_2341&PID_003E\5&1C6E4ACC&1&1
Driver KeyName           : {36fc9e60-c465-11cf-8056-444553540000}\0015 (GUID_DEVCLASS_USB)
Driver                   : C:\WINDOWS\System32\drivers\usbccgp.sys (Version: 10.0.14393.0  Date: 2006-06-21)
Driver Inf               : C:\WINDOWS\INF\usb.inf
Legacy BusType           : PNPBus
Class                    : USB
Service                  : usbccgp
Enumerator               : USB
Location Info            : Port_#0001.Hub_#0002
Location IDs             : PCIROOT(0)#PCI(1A01)#USBROOT(0)#USB(1), ACPI(_SB_)#ACPI(PCI0)#ACPI(USB4)#ACPI(URTH)#USB(1)
Container ID             : {e010817c-7873-11e7-98f3-001e3790fa1d}
Manufacturer Info        : (Standard-USB-Hostcontroller)
Capabilities             : Removable
Address                  : 1
Problem Code             : 10 (CM_PROB_FAILED_START)
Power State              : D3 (supported: D0, D2, D3, wake from D0, wake from D2)

      ------------------ Device Descriptor ------------------
bLength                  : 0x12 (18 bytes)
bDescriptorType          : 0x01 (Device Descriptor)
bcdUSB                   : 0x200 (USB Version 2.00)
bDeviceClass             : 0x00 (defined by the interface descriptors)
bDeviceSubClass          : 0x00
bDeviceProtocol          : 0x00
bMaxPacketSize0          : 0x40 (64 bytes)
idVendor                 : 0x2341
idProduct                : 0x003E
bcdDevice                : 0x100
iManufacturer            : 0x01
 *!*  string descriptors are not available because device is in low power state
iProduct                 : 0x02
 *!*  string descriptors are not available because device is in low power state
iSerialNumber            : 0x03
 *!*  string descriptors are not available because device is in low power state
bNumConfigurations       : 0x01

ConfigDescriptor Error   : ERROR_GEN_FAILURE

prasimix, 2017-08-26:
Hm, not sure about "edge/corner" case, do you have by chance some other Arduino Due board to test it?

jlegen, 2017-08-27:
Tried with another Arduino Due - exactly the same behaviour - only prog port working with isolator.
So imo it could be something with
- internal micro USB header cable (imo unlikely, since it works with prog port (?))
- USB port at case's back (imo unlikely, too)
- Adum isolator

prasimix, 2017-08-27:
You're right, and I believe the first two case should be easy to check. The latest one will require new IC or some scope measuring and probing. Maybe it's also possible that some e.g. "dirt" or other irregularity can be found on the PCB with simple visual check.

jlegen, 2017-08-29:
Dismounted the pcb at the back, it looked absolutely nice and clean. Resoldered Adum and surrounding passives anyway, and cleaned all with isopropanyl afterwards. No change... :-/
Probably unrelated, but i noticed while checking continuity for USB connection:
- while the USB housing at the back is grounded to earth, the metal front metal bezel for the display is not (front metal plate has contact, though)
- the "shield" pin (5) of the USB connection cable to the back pcb seems not to be connected to anything (seems ok according to schematics?)

prasimix, 2017-08-29:
Correct, neither of them are connected to the earth.

jlegen, 2017-08-30:
i soldered a new micro USB header cable, just to be sure; same result/no native port; running out of ideas - apart from throwing a scope onto it... 8-}

prasimix, 2017-08-30:
If it works flawlessly with _programming_ and not _native_ port then only proper port selection under **Tools... Board** menu is missing. No other ideas so far.

jlegen, 2017-09-01:
I did some further "research" - i have an external USB isolator module, which happens to use the exact same Adum3160.
And guess what, this thing behaves exactly the same like the EEZ-PSU, with PSU's Due and also with another standalone Due board. 

It also turned out that "software" doesn't matter - the same Win10 system which does not work with Adum+Due-native does also not work with a current Linux on the same hardware.

What is however interesting - while the "Due Prog port" through Adum is detected as "USB Fullspeed" (= USB 1.1), the native port is "USB Highspeed" (= USB 2.0). This at least could explain why the Adum behaves differently for prog and native port...

I also found some sort of solution - i dug out a very old laptop which i kept for, well, things like that :), and this laptop is able to properly work with Due's native port with the Adum in between.

Knowing this, i then attached the Due-native to an USB-2 port sitting directly on the mainboard of my Win10 system (which did fail before, using the front panel ports)  - and this setup also worked!

So the outcome probably is - the Adum simply seems to be a bit picky regarding the USB standard. Avoiding USB ports broken out with headers or hubs seem to help at least sometimes. 
My regular laptop however - the system which i use in the lab - still does not work, and "swapping" USB ports is obviously not possible there.

But i think i will now leave the PSU at native port, doing SCPI-tests and fw updates with the old laptop (XP, uh.. :o) mentioned above...

prasimix, 2017-09-01:
Thx, for additional info. Regarding SCPI testing please note that you can do it over Ethernet too.

closed 2020-01-20 by prasimix

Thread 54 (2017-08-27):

eez-open/psu-hw #54: self-test not passed

ulaker, 2017-08-27:
access to reset switch obstructed by display board.
Front pannel bottom screws misregistration difficulties to allign threaded part with the case.
Unkeyed and unmarked pin connectors no easy way to determine right orientation. 
First power up resulting in message self-test not passed for sd-card, rtc, both channel ioexp and adc
Troubleshooting guide not mentioning  path to follow for these cases.

prasimix, 2017-08-27:
This is four, not one issue. Please don't do that next time since that makes it difficult to follow up and other people will have difficulties to follow and could add duplicated issues.

> access to reset switch obstructed by display board.

I'm aware of that, but currently there is no remedy for it. If you need reset in the future you still have enough room to access it with sort of paperclip.

> Front pannel bottom screws misregistration difficulties to allign threaded part with the case.

Duplicate, see #52 

> Unkeyed and unmarked pin connectors no easy way to determine right orientation.

Please elaborate. Also consult Fig. 13 and Fig. 24 ([Draft 0.9](http://www.envox.hr/eez/bench-power-supply/group-buy-kit-assembly.html)).

> First power up resulting in message self-test not passed for sd-card, rtc, both channel ioexp and adc
> Troubleshooting guide not mentioning path to follow for these cases.

SD card is possibly not plugged in correctly, check it once again, if still have report error, try to test it on PC/notebook that is equipped with SD card reader.
For Power boards (channels) error, check once again if they are plugged correctly into Arduino Board (sometimes is possible that connectors are shifted up for one position). If you still have a problem, start with checking channel input power (connector X1) where you should have +48 Vdc, and then bias voltages on the output of IC4 (position FB1, FB2, and FB3).

ulaker, 2017-08-27:
Sorry, new here. f
The cable connectors seem sorted now. part  my fault confusion from so many places where I thought it is documented. 

From my perspective the mechanical issues are cosmetic and can be closed as far as I am concerned since I do not expect changes to apply to my kit.

tried to narrow it down by disconnecting sd-card and power boards, still get the rtc self-test not passed. The communication on the spi bus is seemingly not working. Will take some time to locate components that could be detached to isolate the problem.
  
SD card tested separately and seems to be formatted and working on a different environment. 

Power +48V nominal on both boards available.

prasimix, 2017-08-27:
Ok, try to unplug Power boards and power up just Arduino shield and see if e.g. RTC selftest error is still there.

ulaker, 2017-08-27:
Done that. Also disconnected sd card.
Still no response from rtc 
Home menu reachable tried to set time/date also error.

prasimix, 2017-08-27:
If SPI communication is an issue, did you also receive EEPROM seltest error?

ulaker, 2017-08-27:
Initially for several iterations of power up sequences the eeprom was there 
Since early this morning no longer in the list of the self-test not passed.

prasimix, 2017-08-27:
Hm, then it's possible that something related to RTC. You can try to upload test sketch that set date and time and display on the serial monitor new date/time every one second.

``` arduino
#include "SPI.h" // necessary library
#include <eez_psu_rev.h>
#define EEZ_PSU_SELECTED_REVISION EEZ_PSU_REVISION_R5B12 // change to EEZ_PSU_REVISION_R1B9 for older revision
#include <eez_psu.h>

#define RD_CONTROL_1 B10010000
#define WR_CONTROL_1 B00010000
#define RD_CONTROL_2 B10010001
#define WR_CONTROL_2 B00010001

#define RD_SECONDS B10010010
#define WR_SECONDS B00010010
#define RD_MINUTES B10010011
#define WR_MINUTES B00010011
#define RD_HOURS B10010100
#define WR_HOURS B00010100

#define RD_DAYS B10010101
#define WR_DAYS B00010101
#define RD_WEEKDAYS B10010110
#define WR_WEEKDAYS B00010110
#define RD_MONTHS B10010111
#define WR_MONTHS B00010111
#define RD_YEARS B10011000
#define WR_YEARS B00011000

#define RD_CLKOUT B10011101
#define WR_CLKOUT B00011101

unsigned int seconds;
unsigned int minutes;
unsigned int hours;
unsigned int day;
unsigned int weekdays;
unsigned int month;
unsigned int year;

void setup()
{
  eez_psu_init();

  // Initialize serial communication
  Serial.begin(9600);
  // wait until the serial stream is not open
  while (!Serial);
  Serial.println("Serial com ready");

  SPI.begin(); // wake up the SPI bus
  SPI.beginTransaction(PCA21125_SPI);
  digitalWrite(RTC_SELECT, HIGH); // Select PCA21125
  SPI.transfer(WR_CONTROL_1);  // Write mode, a pointer to the address 00h
  SPI.transfer(B00001000);
  SPI.transfer(B00000000);

  // Set hours, minutes and seconds to 16:10:00
  SPI.transfer(B10000000); // Seconds=00; RF - clock integrity is not guaranteed
  SPI.transfer(0x00); // Minutes
  SPI.transfer(0x12); // Hours, 24-hour format

  // Set day, day of week, month and year to 17.07.2015
  SPI.transfer(0x23); // Days
  SPI.transfer(0x01); // 5, is Firday
  SPI.transfer(0x05); // Months
  SPI.transfer(0x16); // Years
  digitalWrite(RTC_SELECT, LOW); // Deselect PCA21125

  delay(2);

  digitalWrite(RTC_SELECT, HIGH); // Select PCA21125
  // Read day, month and year
  SPI.transfer(RD_DAYS);
  day = SPI.transfer(0x00);
  weekdays = SPI.transfer(0x00);
  month = SPI.transfer(0x00);
  year = SPI.transfer(0x00);
  digitalWrite(RTC_SELECT, LOW); // Deselect PCA21125
  SPI.endTransaction();

  // Display received date
  // HEX format is used since results are BCD encoded
  Serial.print("20");
  Serial.print(year, HEX);
  Serial.print("-");
  Serial.print(month, HEX);
  Serial.print("-");
  Serial.println(day, HEX);
  Serial.print("Day of week:");
  Serial.println(weekdays, HEX);

}

void loop()
{
  SPI.beginTransaction(PCA21125_SPI);
  digitalWrite(RTC_SELECT, HIGH); // Select PCA21125
  SPI.transfer(RD_SECONDS); // Read mode, a pointer to the address 02h
  seconds = SPI.transfer(0x00);
  minutes = SPI.transfer(0x00);
  hours = SPI.transfer(0x00);
  digitalWrite(RTC_SELECT, LOW); // Deselect PCA21125
  SPI.endTransaction();

  // Display received time
  // HEX format is used since results are BCD encoded
  Serial.print(hours, HEX);
  Serial.print(":");
  Serial.print(minutes, HEX);
  Serial.print(":");
  Serial.println(seconds, HEX);
  delay(1000);
}

ulaker, 2017-08-27:
Sorry not in the position to follow these instructions immediately. First I need to set up and get working the development environment.

jlegen, 2017-08-27:
Regarding SD card - i also had it failing on power-up after i upgraded to FW 1.01. It turned out that i only had the '2nd newest' SD library on my system. Upgrading by IDE's library manager solved that.

prasimix, 2017-08-27:
@ulaker: The easiest way to get all needed headers and files is to upgrade your firmware to 1.01. Follow instructions [here](http://www.envox.hr/eez/bench-power-supply/building-instructions.html#instr_fw) and mind discussion about external libraries [here](https://github.com/eez-open/psu-firmware/issues/159).

@jlegen: Please provide more information what you actually did, and which Arduino IDE you are using, that I can include that into assembly instructions.

jlegen, 2017-08-27:
- I installed Arduino IDE 1.8.4
- grabbed firmware 1.01 and both libs from eez psu github
- grabbed ethernet2 from your other gihub
- compiled 1.01 - no errors
- uploaded firmware (worked using prog port)
- psu selftest: SD card error
Since this did not give an error with the pre-installed FW 1.00, i was pretty sure that the problem was on my side. Looked into the eez psu sketch and found, that this self test failure is generated right with/after creating the SD object. 
Then i had a look into the library manager of the arduino IDE and noticed an upgrade for SD lib from 1.1.0 to 1.1.1 (if i remember correctly) - upgrade, recompile, reflash, error gone!

My guess: IDE 1.8.4 is delivered with SD 1.1.0, which seem to have an issue, so they provided an updated version 1.1.1 right after. 
Usually, the IDE also shows a notice for upgrades, but this may take a while from my experience....

ulaker, 2017-08-27:
Hello prasimix,

found some time and managed to compile the rtc test sketch that you provided. Looks the rtc is responding with settings and is updateing the time in one second intervals. This I tested with the arduino and the  front pannel assembly detached and powered from the usb port of the development pc. 

So this would mean the spi communication to the rtu is ok at least as long as no other peripheral attached. 

Of course i lost the factory delivered  firmware.
 The development environment seems not set up correctly since github version of the firmware is not compiling without error 

Arduino: 1.8.4 (Linux), Board: "Arduino Due (Programming Port)"

/home/erich/Arduino/eez_psu_sketch/eez_psu_sketch.ino:31:23: fatal error: Ethernet2.h: No such file or directory
 #include <Ethernet2.h>
                       ^
compilation terminated.
exit status 1

ulaker, 2017-08-27:
found and installed one Ethernet2 library, probably not the right one since compilation aborts with:
Arduino: 1.8.4 (Linux), Board: "Arduino Due (Programming Port)"

sketch/ethernet.cpp: In function 'void eez::psu::ethernet::init()':
ethernet.cpp:146: error: 'class EthernetClass' has no member named 'setDhcpTimeout'
     Ethernet.setDhcpTimeout(ETHERNET_DHCP_TIMEOUT * 1000UL);
              ^
exit status 1
'class EthernetClass' has no member named 'setDhcpTimeout'

this is way above my level at this time.

electrokean, 2017-08-27:
@ulaker use latest Ethernet2 library from here: https://github.com/eez-open/Ethernet2/releases
See discussion on your error here: https://github.com/eez-open/psu-firmware/issues/159

ulaker, 2017-08-27:
thanks, this did indeed help with compiling and installation of firmware version 1.01
unfortunately power up resulting in message self-test not passed for sd-card, rtc, both channel ioexp and adc did not change. 
In addition playing with the menues enabled ethernet and am no stuck probably with the startup not getting past the dhcp since I do not have a dhcp server to help get past this stage in the power up process. Pressing reset does not help to get out of the loop. Is there another whay to force to continue without ethernet when it is enabled?

ulaker, 2017-08-27:
EUREKA some magic worked while I was typing the above. The ethernet setup must have timed out and now it seems to be in a happily working (uncalibrated) state. 
I am now working up and exploring all the options. 
But first I will redo the mechanical assembly and hope to be able to do everything else with all the screws in place.

Thank you all for prompt support and the patience and understanding you had with me.

ulaker, 2017-08-28:
Well, one night later back to square one? After getting excited yesterday late at night with the success in running up the new toy got back to self-test not passed upon switching on this morning. Looks like something is at odds with the timing when and how long the power up self-test routine decides upon pass/fail? More work required in this area I am afraid. 
[image]

prasimix, 2017-08-28:
It's very highly unlikely that you have a "timing issue". The PSU can continuously works for days and weeks without any "timing issue". It's more likely that you have a problem with some connectivity between Arduino Due and Arduino Shield, especially 6-pin header in the middle where are SPI lines. Inspect it and eventually apply some "contact/degreaser" spray such as [KONTAKT WL](http://www.tme.eu/en/details/wl_200/cleaning-maintaining-products/kontakt-chemie/71009-002/).

ulaker, 2017-08-28:
disassembled front pannel and inspected the arduino,  shield and the display module. SD-card socket is a bit flimsy, at least the card does not seem to be firmly hold in place. But I assume it is good enough for the purpose here. The SPI connector also looks optically and electrically (continuity) ok. re-assembled and now EEPROM is no longer on the list of the failed self-test items (CH2 ADC also visible now) Next I would capture some traffic on the bus but I am not equipped here with the required toys.

prasimix, 2017-08-28:
SPI connector in the middle just carry general SPI signals: CLK, MOSI and MISO. Other important signal is "chip select" and each SPI peripheral has it's own line and they are distributed all around as you can see on [Sheet 9](https://raw.githubusercontent.com/eez-open/psu-hw/master/Consolidated/EEZ%20PSU%20consolidated%20r5B12%20Sheet%209of12.png).

ulaker, 2017-08-28:
Another question is the calibration password. When I enter it correctly  it immediately  ask for new and also repeat the new assword? I do not want to change I actually tried to exercize the routine to calibrate the channel. Is it compulsory chnage password associated with that?

prasimix, 2017-08-28:
You want to say that when you enter Calibration wizard that it ask you to change password? I'm not aware of that "feature" :) Can you provide some short video?

ulaker, 2017-08-28:
Maybe it is misunderstanding on my side. The system settings menu item **channel calibration** might be just the password management only and not the  **calibration wizard**. That one is possibly now behind the big red ERROR part. I could technically capture a video clip, but I need to find some fixture to hold and point  the camera to do that, maybe later, in this case it is probably not useful.

prasimix, 2017-08-28:
Ok, now I understand, no video is needed. 
The system settings menu include both calibration password change and each channel calibration options. If you select "Calibration password" change you'll be able to set new password. Please note that will be the _only_ option available/visible on that page if both channels failed to pass selftest.

ulaker, 2017-08-28:
Thank you for patiently educating me. Would take much longer to find this all out myself by reading it somewhere. I might try to find a trypod or improvize some fixture to be able to forward vidoe of the somewhat un-deterministic  behaviour on repeatedly pressing reset butoon (the one on the upper corner of the arduino board. In a substantial number of iterations of the startup from reset it seems to reach the point where it asks if I want to do channel calibration any touch of the screen than transits to standby and black screen followed by startup with self-test error sometimes with jus the channels and most of the time rtc and sd-card also

prasimix, 2017-08-28:
You have to check all connections. When everything is in place you can reset/restart it as much as you want and it should pass selftest every time without exception.
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

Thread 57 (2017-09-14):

eez-open/psu-hw #57: X12 X14 Pin confusion

dagema, 2017-09-14:
I am confused/concerned about the schematic references to connectors X12 and X14.  According to the schematic, pin X12-8 is connected to AUX1_USET_IN, but in fact it is (properly labeled on the case) connected to (external trigger) GND, which according to the schematic should be connected to X12-1 (casing label "Remote prog.").  Similarily, X12-4 and X12-5 (Sense+ and Sense-) appear to be reversed when compairing actual wiring with the schematic. Also pin X12-6 does not go to R177 /unless you count the pins from right to left).  The same also apply for the X14 connector.  Summarizing, its seems that "Remote prog" and "Ext. trigger" are reversed in the schematic as well as "Sense+ with "Sense-",  for both X12 and X14. I am referring to the "EEZ PSU consolidated rB12.pdf" file for the schematic references, and the  video demonstrating the "External/remote voltage programming" which infers X12 pin numbering as going from 1 to 8 from counting from left to right.  So now I ask, what is right? The schematic pin assignments and labeling match if you count from right to left, but the that does not seem to match the video, which obviously seems to work as expected and looks as if counting from left to right!  Very confusing.

prasimix, 2017-09-14:
Please note that both X12 and X14 are mounted on the bottom (reverse!) side of the PCB. Therefore pin numbers are mirrored. What is marked on the front panel over push-in 8-pin connectors are correct. The easiest way to check it is by activating remote sensing. If that terminals are swapped reverse polarity detection circuit (Q18, Q20 on Sheet 5/12) will instantly generate error!

dagema, 2017-09-15:
OK, so if I understand you correctly, the labelling on the case reads from left to right, so that pin 1 according to casing label is actually pin 8 according to schematic. If that is true, then I am now clear and satisfied.

closed 2017-09-15 by dagema

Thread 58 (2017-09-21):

eez-open/psu-hw #58: Minor: one connector orientation unclear from assembly instructions

raplin, 2017-09-21:
Wow just built mine in an hour and.. perfect!  Extremely impressed.  Anyway, very minor thing; unless I missed it in the assembly instruction PDF, the orientation of unpolarized header A2 where it connects to  the front panel board is not at all obvious. If you zoom in on one of the photos you can just about see which way up it is, but clarification would be useful.
Brilliant kit - very professional

prasimix, 2017-09-21:
Yes, that detail is shown in lower right corner on[ Fig. 24](http://www.envox.hr/eez/images/arduino_shield_cables2.jpg). Feel free to suggest clarification and I'll add it on the web page and PDF doc.

raplin, 2017-09-21:
Ah yes you're right I didn't see the inset image there. Thanks! I'm really impressed with this PSU - the user interface and functionality is even better than I was hoping for.

closed 2017-09-21 by raplin

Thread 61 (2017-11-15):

### ISSUE TITLE
Consider presenting at FOSDEM in 2018

### ISSUE THREAD

**Issue by kasbah** [eez-open/psu-hw#61]
I am very impressed with your project, great job on the documentation! I  thought would let you know that there will be an Open Hardware dev room at FOSDEM next year. Call for participation is available, with links, at https://www.ohwr.org/projects/ohr-meta/wiki/FOSDEM2018

> This is the call for participation in the FOSDEM 2018 devroom on
> Computer Aided Design (CAD) tools and Open Hardware, to be held on
> Saturday 3 February 2018 in Brussels, Belgium. We are looking for
> contributions under the form of talks and tutorials covering the
> following main topics:
>
> - Printed Circuit Board (PCB) design tools (e.g. KiCad and gEDA)
>
> - Analogue and digital simulators (e.g. ngspice, Qucs, Gnucap, Xyce,
> GHDL, Icarus and Verilator)
>
> - Any other EDA tools such as high-level tools for digital hardware
> design (e.g. Migen) and HDL synthesis tools (e.g. Yosys)
>
> - Field solvers such as openEMS
>
> - Mechanical 2D and 3D CAD tools such as LibreCAD, FreeCAD, OpenSCAD and
> SolveSpace
>
> - Open Hardware projects such as the Teres laptop and the lowRISC SoC
>
> - Inter-project opportunities for collaboration
>
> We hope to provide an opportunity for attendees to bring themselves up
> to date on the latest FOSS CAD and Open Hardware developments, share
> knowledge and identify opportunities to collaborate on development
> tasks. This devroom is an evolution of the EDA devroom we organised in
> 2015, 2016 and 2017.

**Comment by prasimix** [comment]
Hi, and thanks for information about FOSDEM. Please note that GitHub issue tracker is not a place for such promotion. You can use our [contact form](http://www.envox.hr/eez/contact-us.html) in the future.

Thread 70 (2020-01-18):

eez-open/psu-hw #70: Expected self test failures

jfitter, 2020-01-18:
I am looking for some advice without having to wade through all of the code in minute detail.
I have built the PSU except for the power modules. For testing I am powering the Arduino Shield from the Native USB port. This enables me to build and upload the code, check that it all works, and communicate using SCPI. All good, and works fine - except....
I expect that certain items will fail self test because they are not there. The display of course works. The RTC works too and keeps time. Many other things work, but the SD card fails self test.
Also the display shows ERROR and does not get past this. I did expect a full but non-functional display.
Is this expected behaviour? Will the SD card work when I get connected to the real power supplies?
I like to check stuff as I progress with the build, so what can I expect to be working just running off the native usb port?
Thanks.

prasimix, 2020-01-18:
SD card test is not related to power modules but to SD card itself. Check if SD card is functional on e.g. PC that accept SD cards. Also take into account that display's SD card socket may has no contact or that SD card is not inserted properly.

jfitter, 2020-01-18:
mmm I have fitted an SD card extender cable and brought the socket to the front panel. Maybe the cable is too long. I will check it out. Thanks.

jfitter, 2020-01-20:
Still somewhat confused.
I have two extender cables - short and long - 100mm and 480mm.
I have two LCDs from different manufacturers with different controllers.
All combinations of extender cables and SD card readers work just fine, even with the readers on the end of long USB cables.
All combinations of extender cables and display mounted SD card sockets fail, always.
SD cards inserted directly into display mounted SD card sockets work, always.
An SD card pried apart and carefully soldered to the end of an extender cable fails (to eliminate physical differences between the extender and a real SD card).

There is something about an extender cable that only the display card is incompatible with, regardless of the length of the cable.

Is this likely to be solved in software (timing etc.)?

Any hints would be appreciated.

I think I am missing something here. Is the SD card interface on the LCD display non standard? Is this a drive level issue? Do I need buffers? If so then why does the extender cable work connected to a reader connected to a PC on a 2m USB cable?

prasimix, 2020-01-20:
Communication with SD card on the LCD display is done via SPI. I don't know how USB cable came into picture.

jfitter, 2020-01-20:
SOLVED
The TFT_320QVT display has three 1K resistors in series with the signal lines to the SD card socket - LCD_CS, SCLK, and MOSI. I presume they are there to allow the display to be used with 5V signalling, say with a 5V Arduino. I replaced them with 0R shunts and it now works.

The clue came from the guys on the 3D printer forums who like to extend their SD cards to the front panel. Only the ones extended from the back of the LCD displays failed to work. As far as I can ascertain they have not yet solved their problem.

So, the resistors loaded up the signal lines enough so no amount of extension worked. The only arrangement that worked is if the SD card was actually in the socket. That's a bit of marginal engineering I would say - to save the cost of a buffer.

Maybe this will save someone a lot of time and head scratching.

closed 2020-01-20 by jfitter

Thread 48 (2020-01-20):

### ISSUE TITLE
Grammar fixes for Assembly instructions

### ISSUE THREAD

**Issue by Cabalist** [eez-open/psu-hw#48]
Hey there!  Got My Crowd Supply kit yesterday and just finished assembling it.  I'd like to suggest some clarifications and grammar for the assembly instructions.  Are they located on github?

**Comment by prasimix** [comment]
Sure, it's [here](https://github.com/eez-open/psu-hw/blob/master/Building%20instructions/Complete%20kit%20assembly%20instructions.odt).

**Comment by szwesleyzhao** [comment]
so cool

**Comment by prasimix** [comment]
Nothing happened, closed.

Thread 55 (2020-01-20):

### ISSUE TITLE
Typos in power board description

### ISSUE THREAD

**Issue by Erik-k** [eez-open/psu-hw#55]
(Hope this is the right place to put this) In the description of the power board at http://www.envox.hr/eez/bench-power-supply/power-board.html there are several typos or suspected typos. Entirely possible it's my own ignorance too in which case I'd love to learn. 

First: in "Bias Power Supply" section, third paragraph, since the \ERROR signal is active-low, the sentence "The MCU will not enable power output during start up until that signal is low." sounds wrong and I think it should be "will not enable power until that signal is **high**" which means there is no error. 

Second: "Series/Pass element and control loops" section, third paragraph, the description of how Q4 works doesn't make sense to me and I asked a very experienced analog engineer about it too. Both of us think that the paragraph should be talking about the Vgs not Vgd. Why does the gate need to be so much higher than the drain on an N-FET? Vgs certainly, and the paragraph makes sense if "drain" is replaced with "source". Vgs needs to be positive and ~5V higher gate than source to keep the FET on.

**Comment by prasimix** [comment]
First: this is correct, is should be "**while** this signal is low" or as you suggested "until that signal is **high**"

Second: maybe we should use here needed relation between Vgs and Vds for Q4 as source follower?

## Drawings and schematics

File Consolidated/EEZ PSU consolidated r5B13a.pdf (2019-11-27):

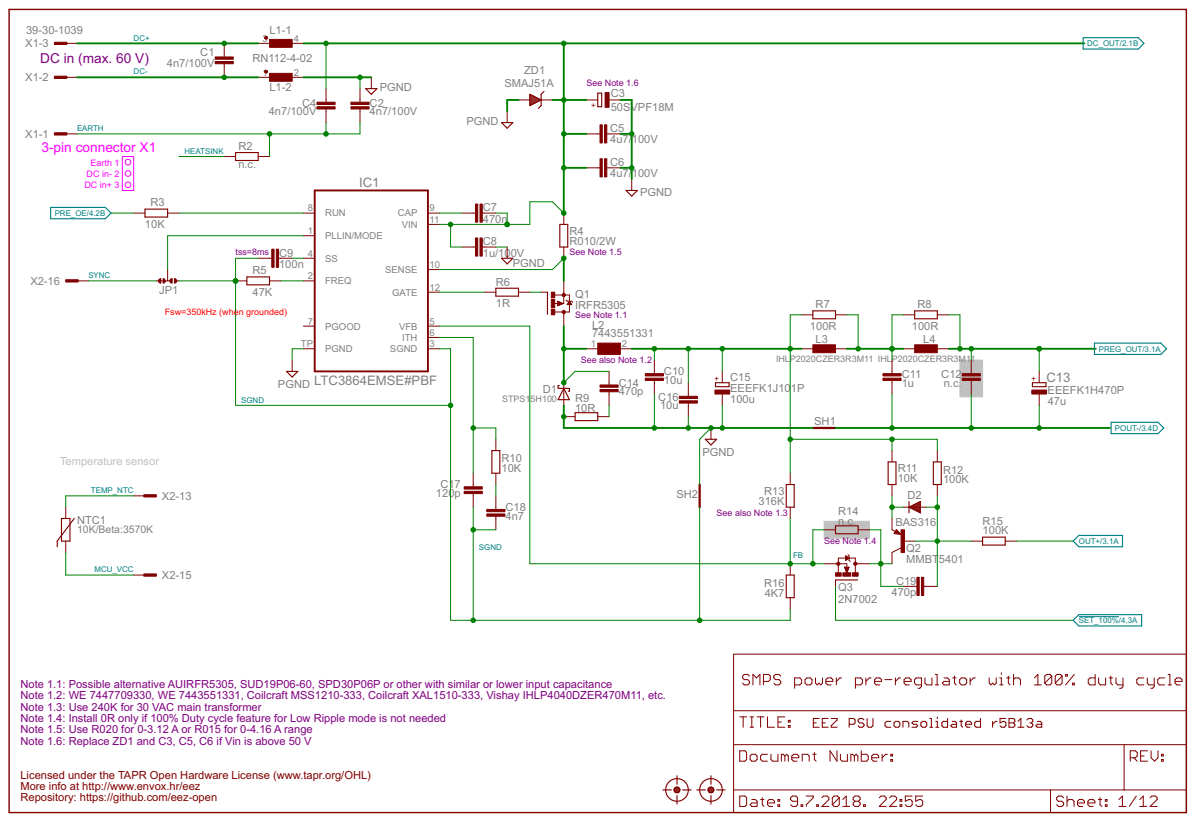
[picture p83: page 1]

EARTH
DC in- 2 DC in+ 3 3-pin connector X1

Note 1.1: Possible alternative AUIRFR5305, SUD19P06-60, SPD30P06P or other with similar or lower input capacitance Note 1.2: WE 7447709330, WE 7443551331, Coilcraft MSS1210-333, Coilcraft XAL1510-333, Vishay IHLP4040DZER470M11, etc. Note 1.3: Use 240K for 30 VAC main transformer

Note 1.4: Install 0R only if 100% Duty cycle feature for Low Ripple mode is not needed
Note 1.5: Use R020 for 0-3.12 A or R015 for 0-4.16 A range
Note 1.6: Replace ZD1 and C3, C5, C6 if Vin is above 50 V

Licensed under the TAPR Open Hardware License (www.tapr.org/OHL)
Repository: https://github.com/eez-open More info at http://www.envox.hr/eez

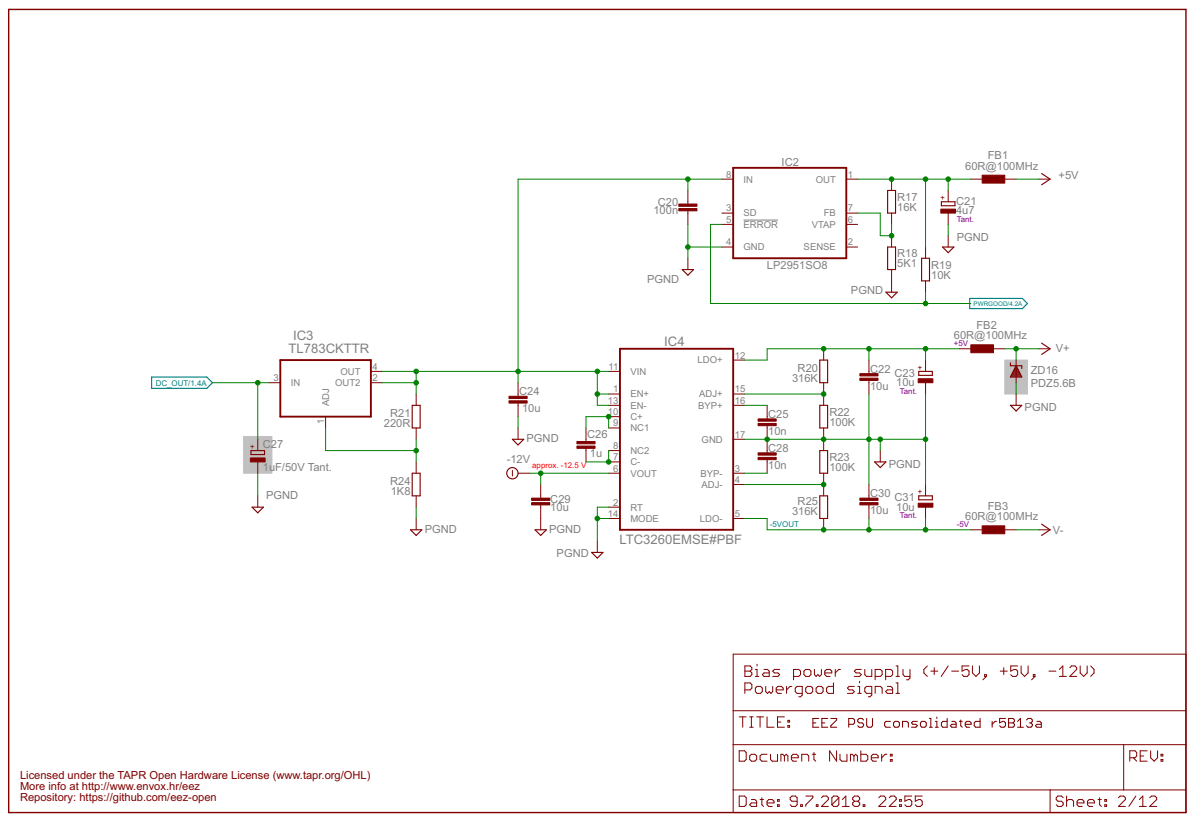
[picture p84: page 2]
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

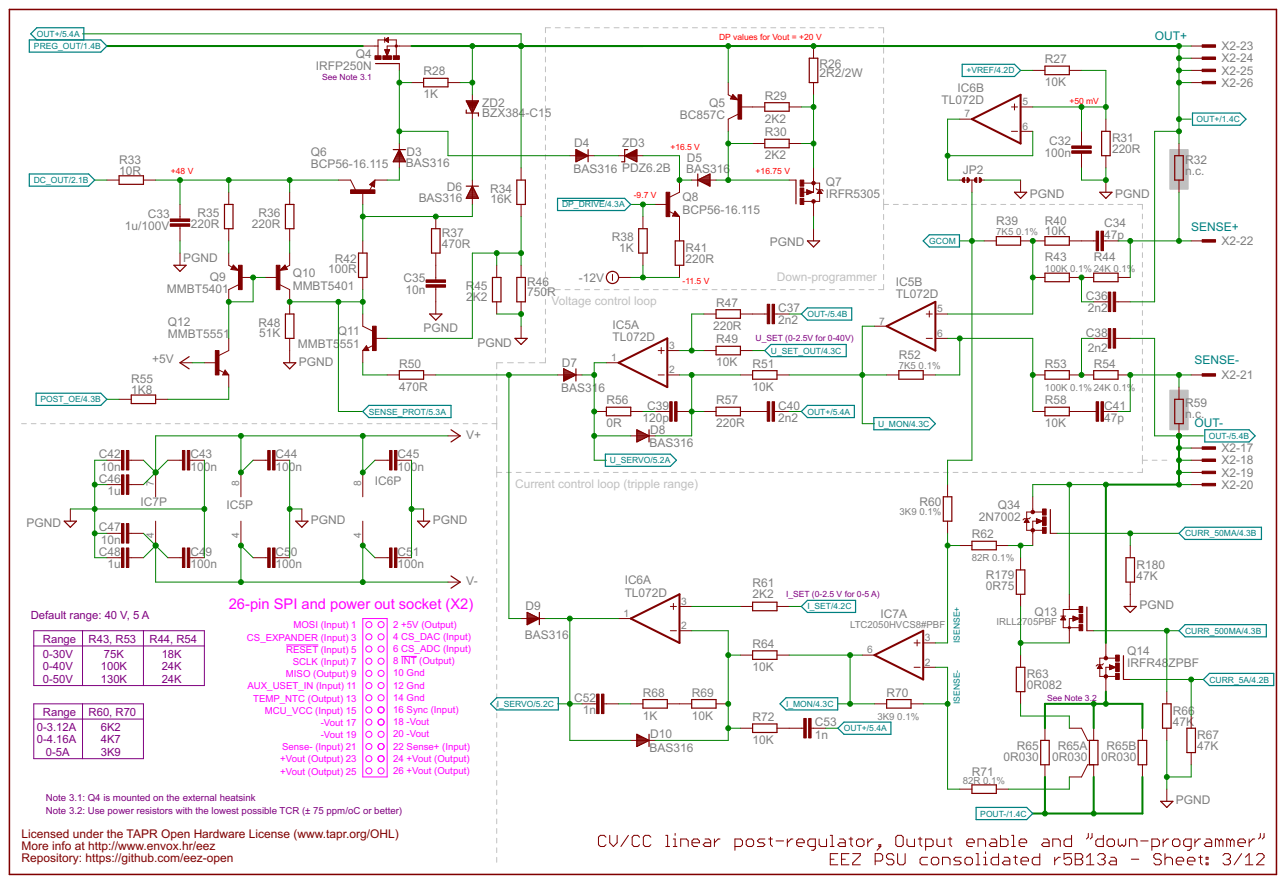
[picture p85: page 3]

DP values for Vout = +20 V

Current control loop (tripple range)

18 -Vout 16 Sync (Input) 14 Gnd Sense- (Input) 21 +Vout (Output) 23 +Vout (Output) 25
-Vout 19 TEMP_NTC (Output) 13

24 +Vout (Output) 26 +Vout (Output) 22 Sense+ (Input) 20 -Vout

Note 3.1: Q4 is mounted on the external heatsink

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

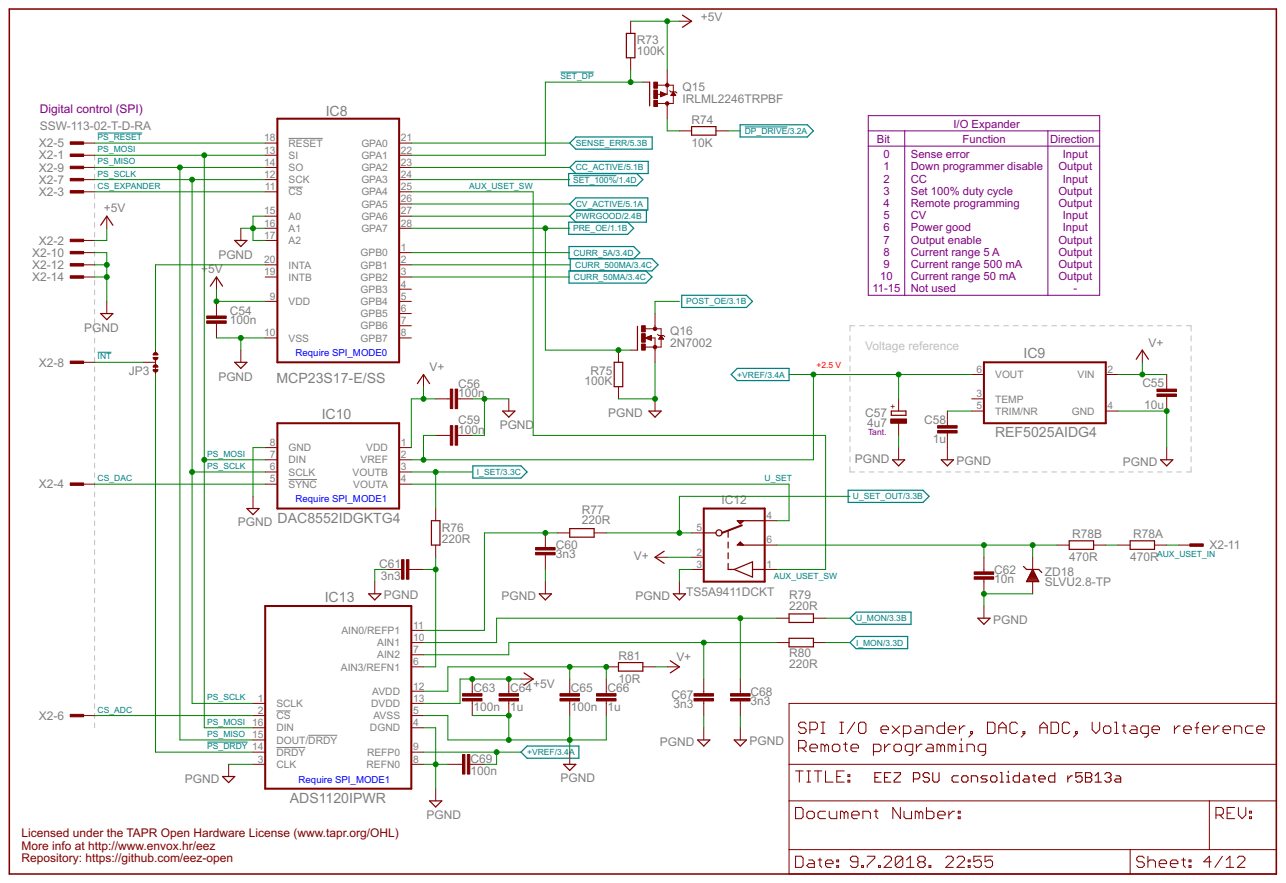
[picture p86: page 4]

Bit | Function | Direction Sense error Input
0 1 2 3 4 5 6 7 8 9 10 11-15 | Down programmer disable CC Set 100% duty cycle Remote programming CV Power good Output enable Current range 5 A Current range 500 mA Current range 50 mA Not used | Output Input Output Output Input Input Output Output Output Output -

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

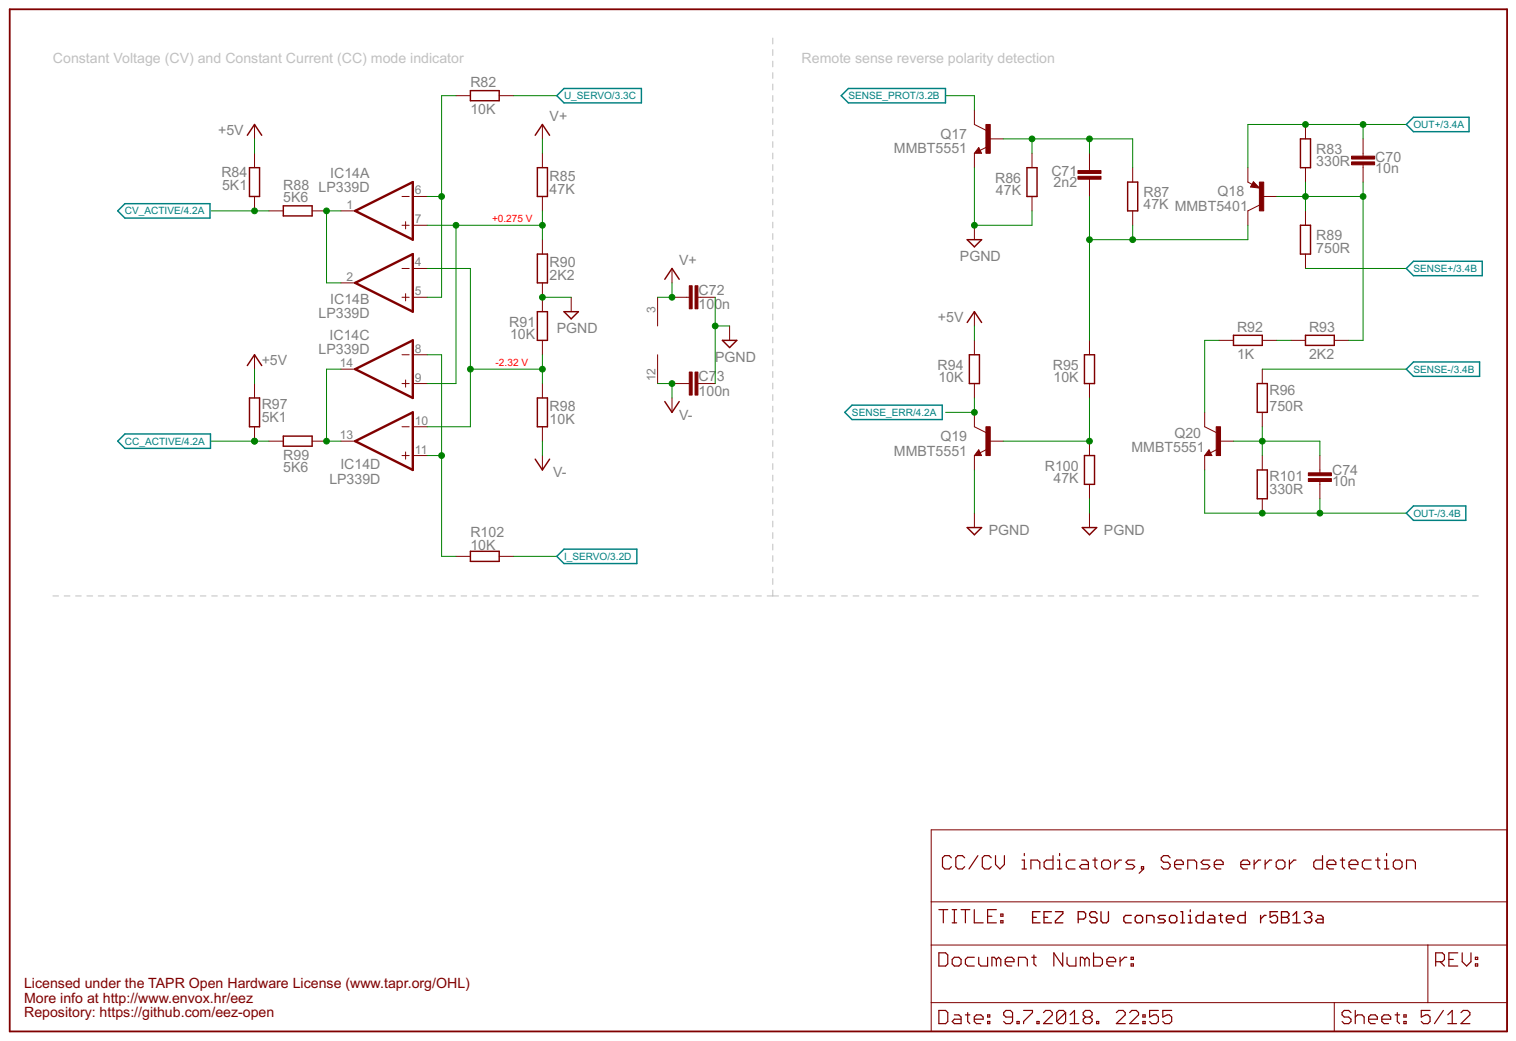
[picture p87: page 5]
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

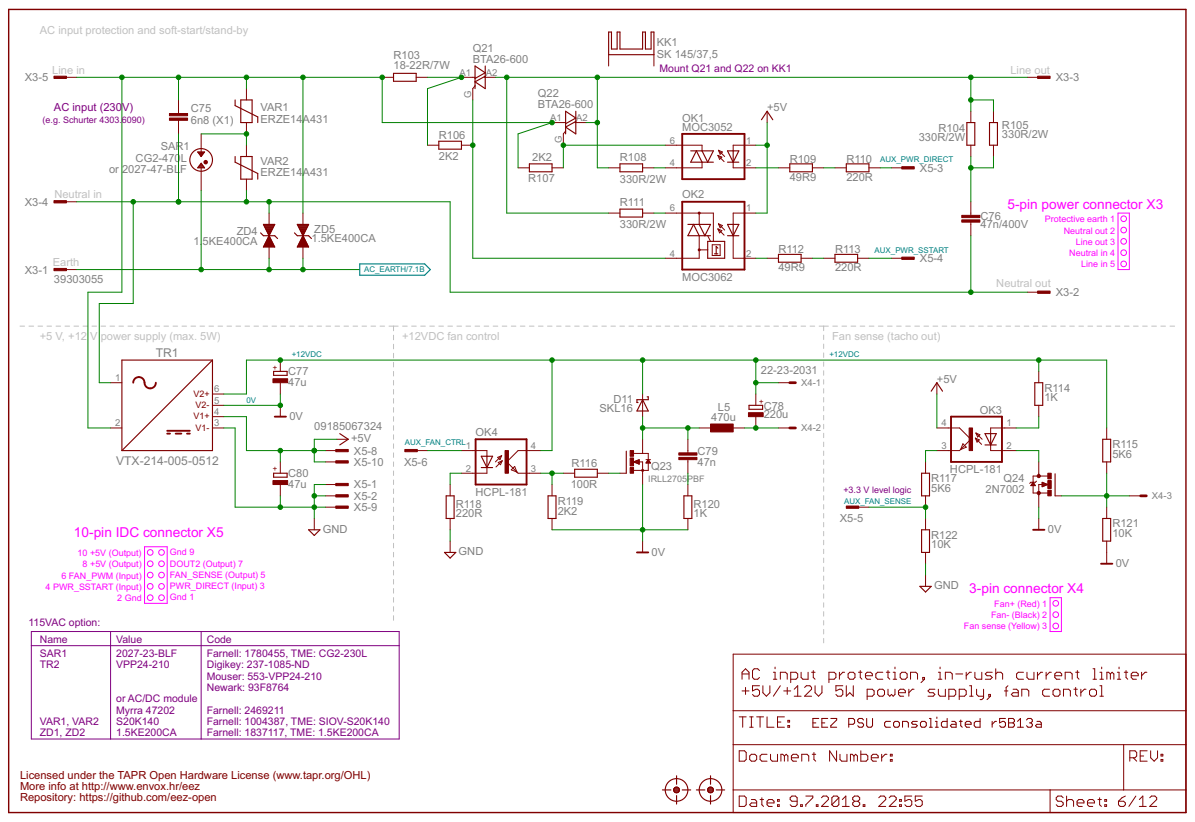
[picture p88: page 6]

AC input protection and soft-start/stand-by

BTA26-600

Protective earth 1 Neutral out 2 5-pin power connector X3

Line out 3 Neutral in 4

115VAC option: TR2 Name | Value | Code

SAR1 VAR1, VAR2 ZD1, ZD2 | 2027-23-BLF VPP24-210 or AC/DC module Myrra 47202 S20K140 1.5KE200CA | Farnell: 1780455, TME: CG2-230L Digikey: 237-1085-ND Mouser: 553-VPP24-210 Newark: 93F8764 Farnell: 2469211 Farnell: 1004387, TME: SIOV-S20K140 Farnell: 1837117, TME: 1.5KE200CA

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

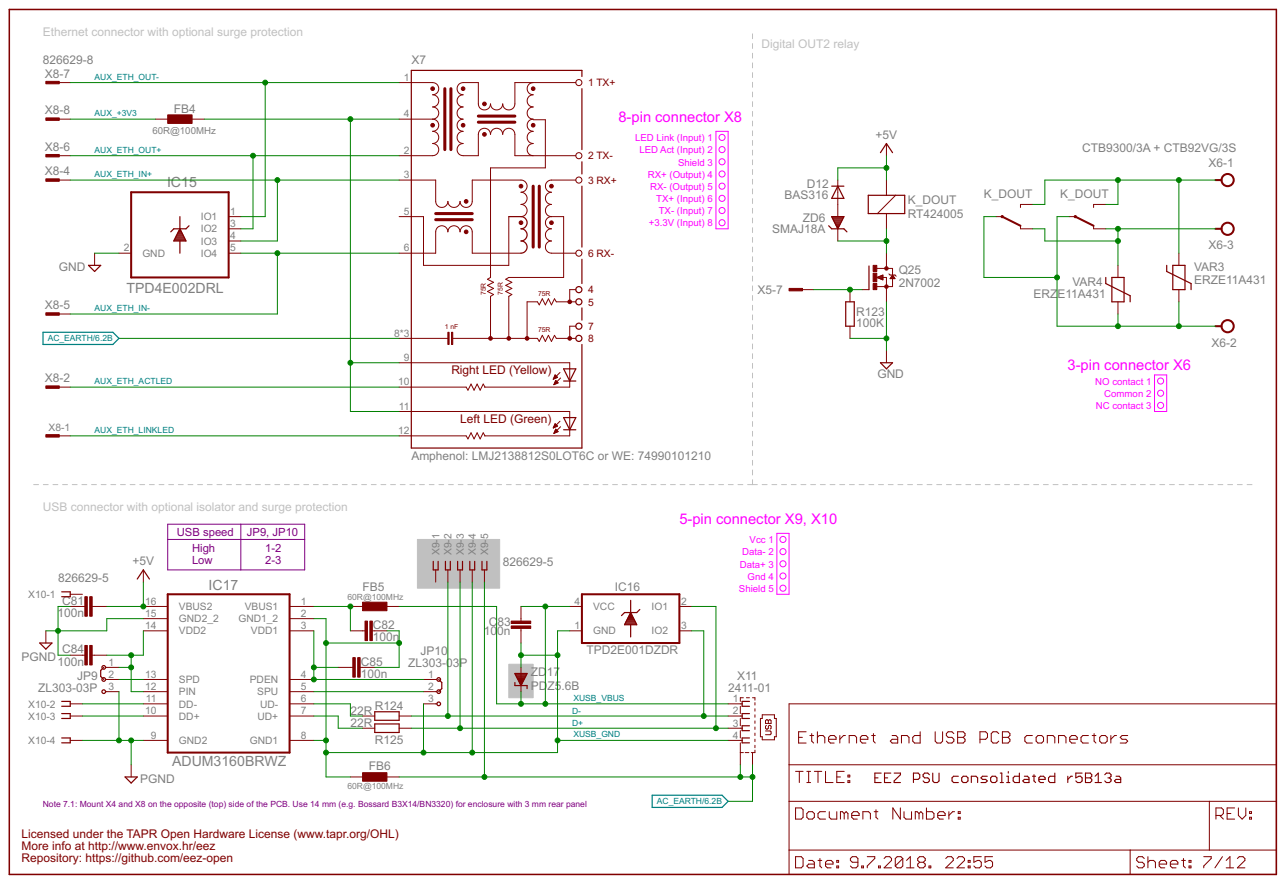
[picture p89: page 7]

Ethernet connector with optional surge protection

LED Link (Input) 1
LED Act (Input) 2 RX+ (Output) 4 RX- (Output) 5 Shield 3

Common 2 NO contact 1 3-pin connector X6

USB connector with optional isolator and surge protection

USB speed | JP9, JP10
High Low | 1-2 2-3

Shield 5 Vcc 1 Data+ 3 Gnd 4

XUSB_GND

Note 7.1: Mount X4 and X8 on the opposite (top) side of the PCB. Use 14 mm (e.g. Bossard B3X14/BN3320) for enclosure with 3 mm rear panel

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

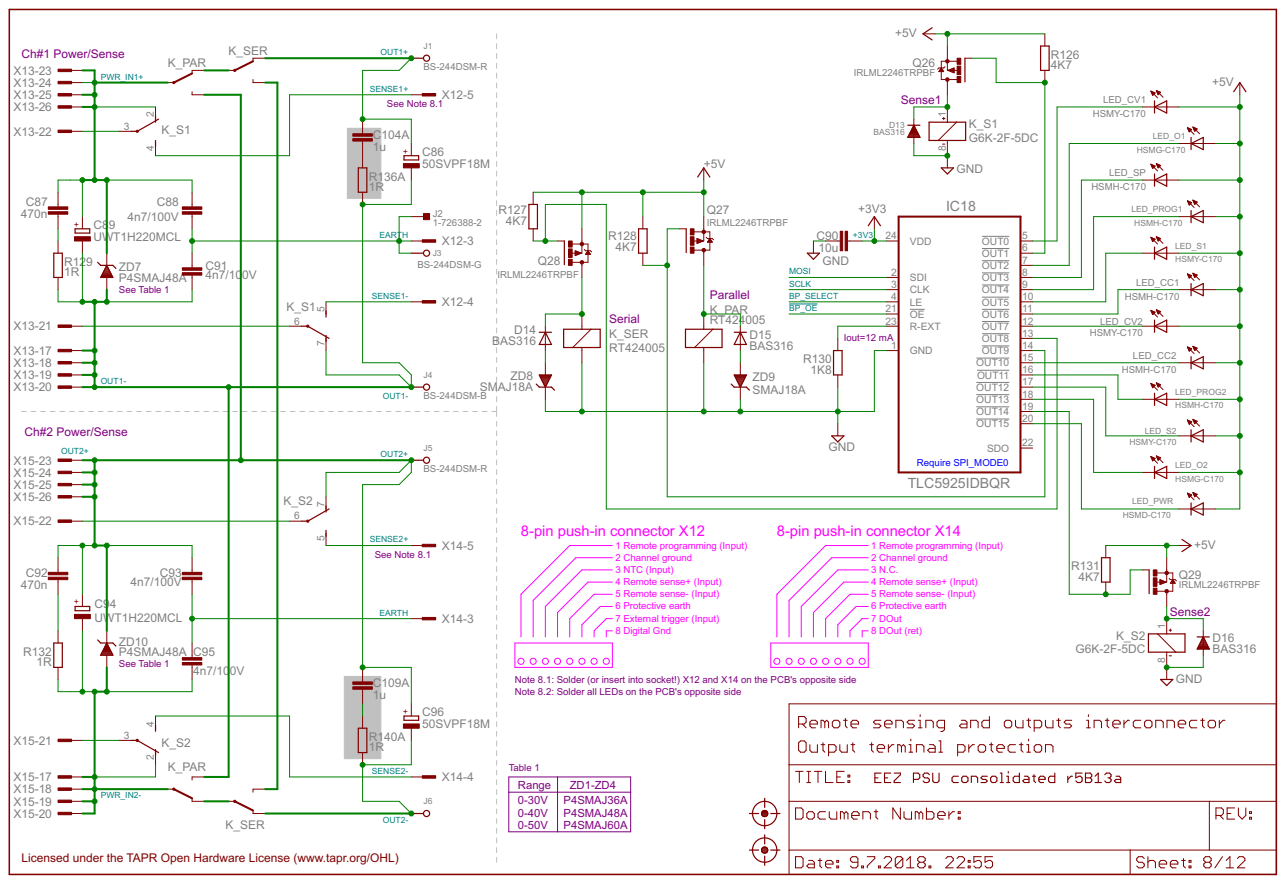
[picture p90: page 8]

8-pin push-in connector X12

1 Remote programming (Input)
5 Remote sense- (Input) 2 Channel ground

3 NTC (Input)
4 Remote sense+ (Input) 6 Protective earth

7 External trigger (Input) 8 Digital Gnd

Note 8.1: Solder (or insert into socket!) X12 and X14 on the PCB's opposite side
Note 8.2: Solder all LEDs on the PCB's opposite side

Range | ZD1-ZD4
0-30V 0-40V 0-50V | P4SMAJ36A P4SMAJ48A P4SMAJ60A

Licensed under the TAPR Open Hardware License (www.tapr.org/OHL)

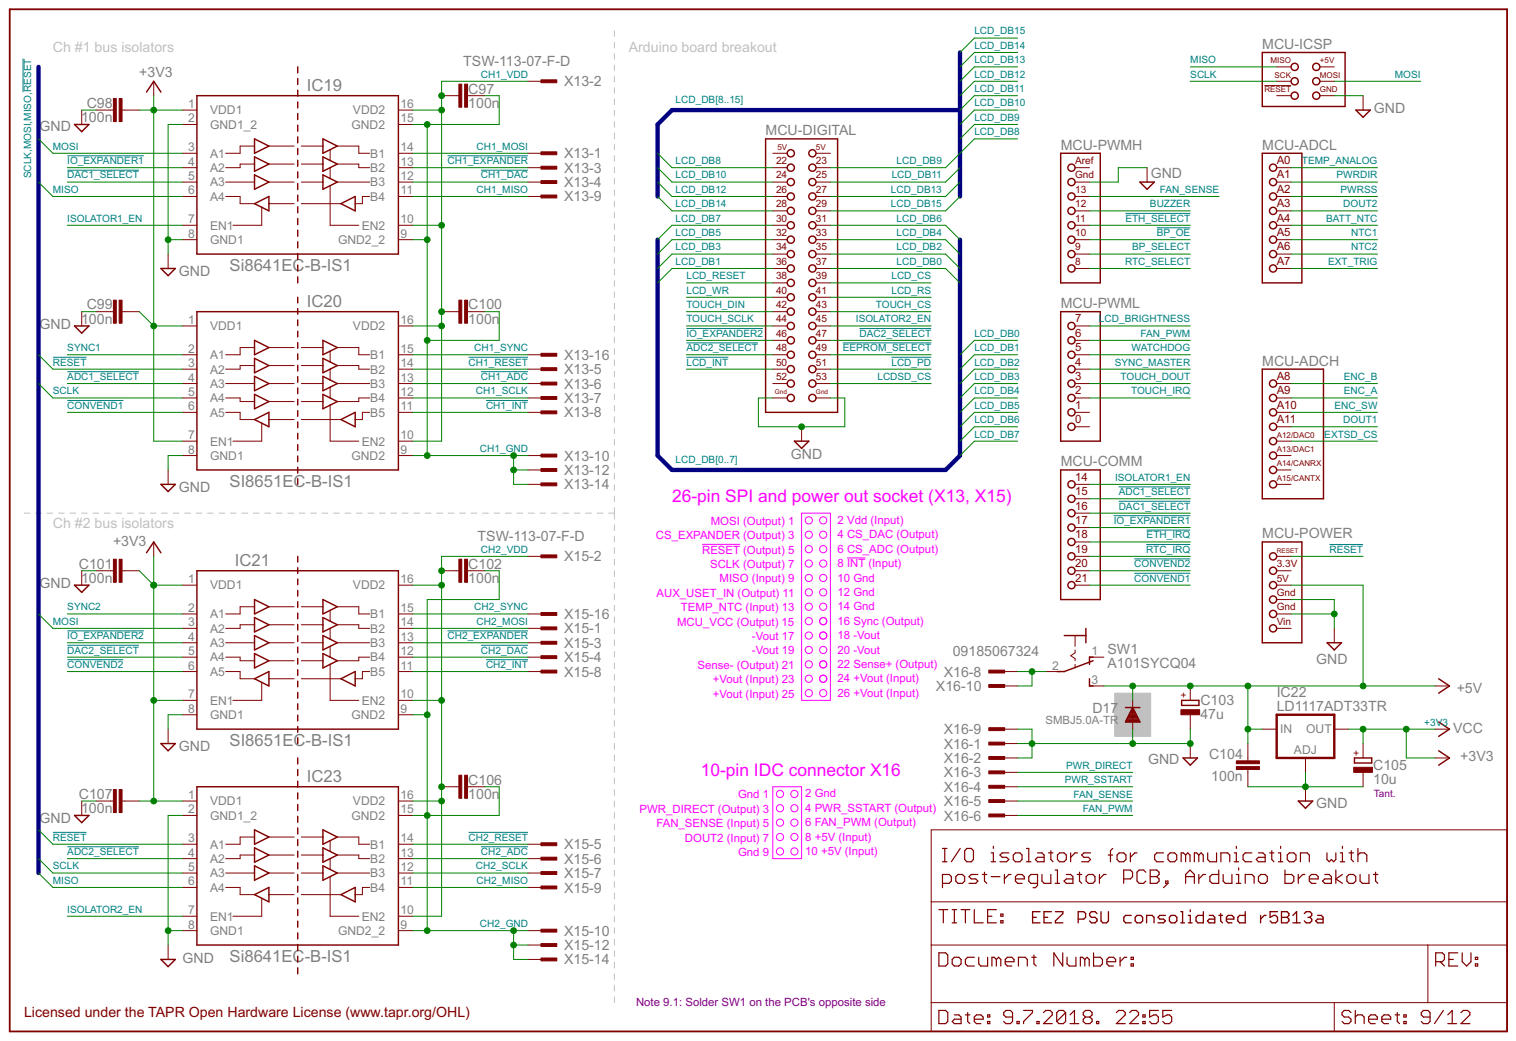
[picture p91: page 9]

SCLK,MOSI,MISO,RESET

2 Vdd (Input) SCLK (Output) 7

18 -Vout 16 Sync (Output) 14 Gnd

24 +Vout (Input) 26 +Vout (Input) 22 Sense+ (Output) 20 -Vout

Sense- (Output) 21 +Vout (Input) 23 +Vout (Input) 25

PWR_DIRECT (Output) 3 FAN_SENSE (Input) 5 10-pin IDC connector X16

Licensed under the TAPR Open Hardware License (www.tapr.org/OHL)

Note 9.1: Solder SW1 on the PCB's opposite side

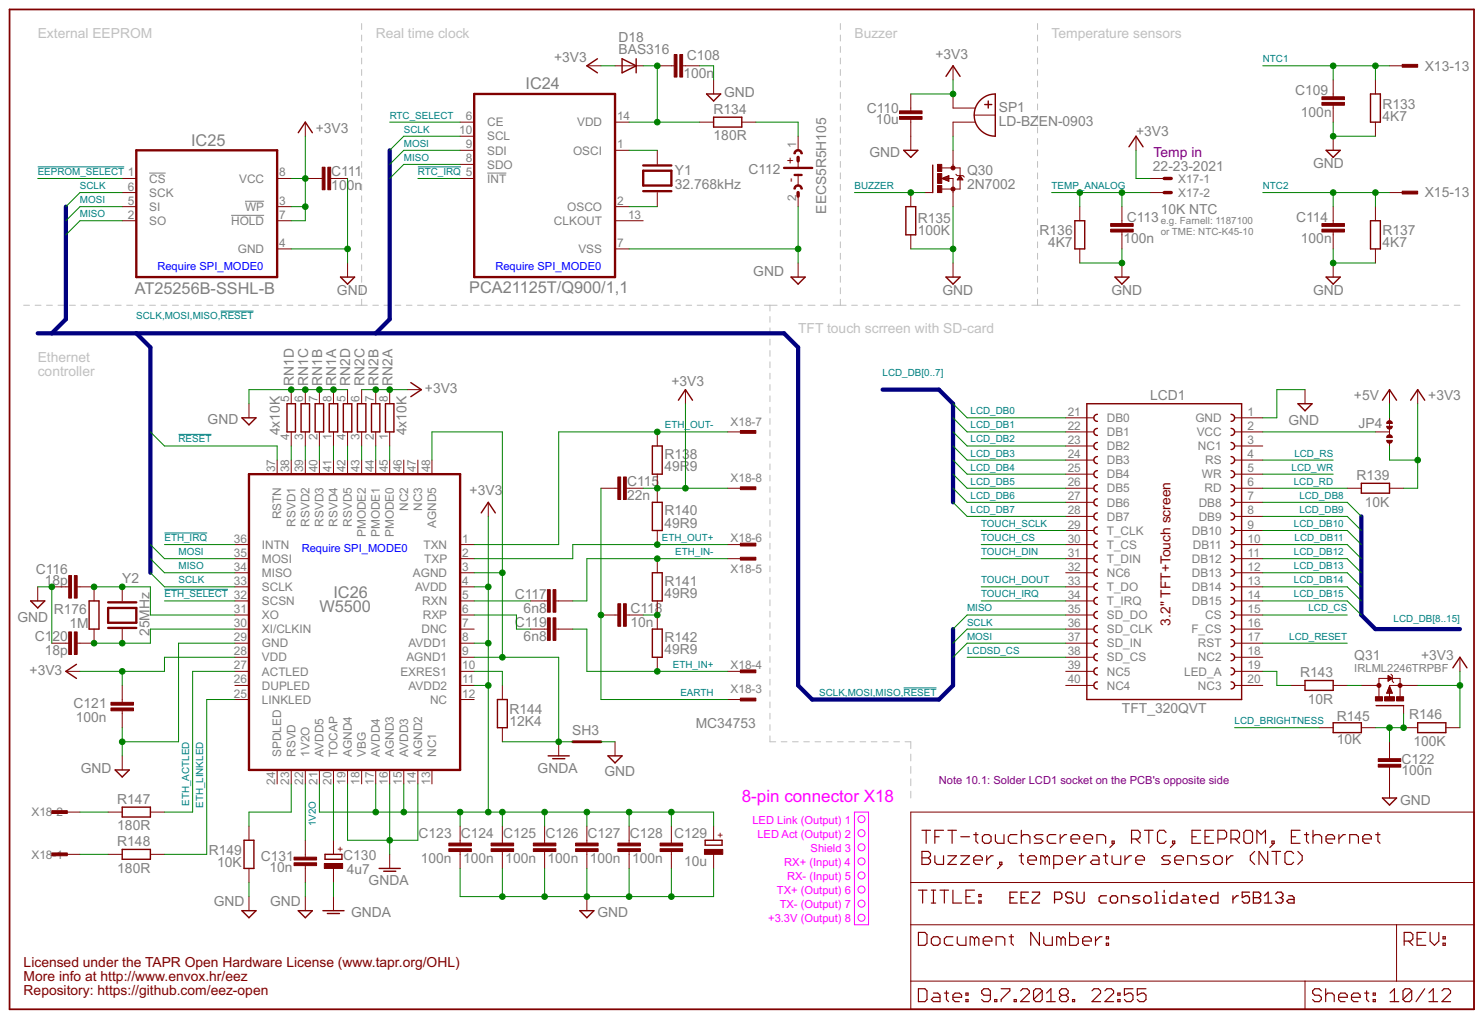
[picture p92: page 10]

SCLK,MOSI,MISO,RESET

TFT touch scrreen with SD-card

Note 10.1: Solder LCD1 socket on the PCB's opposite side

LED Link (Output) 1
LED Act (Output) 2 RX+ (Input) 4 RX- (Input) 5 Shield 3

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

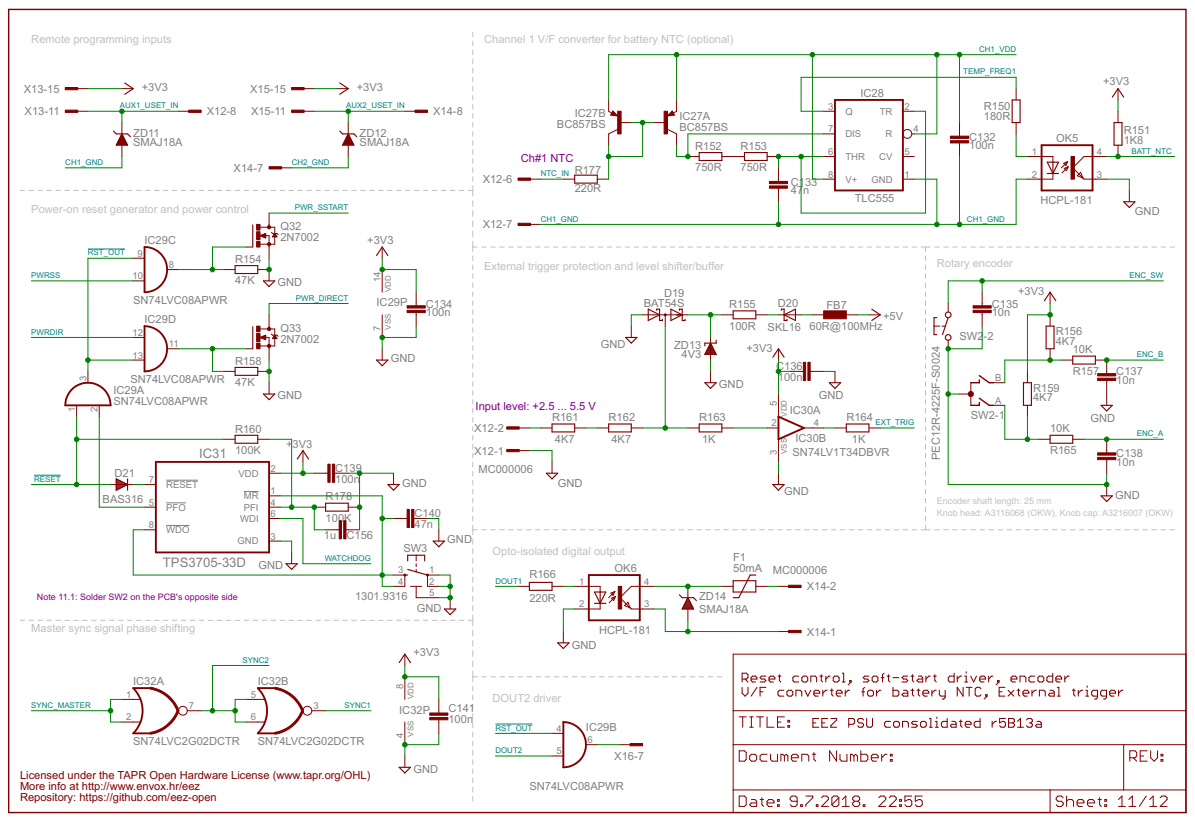
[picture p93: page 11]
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

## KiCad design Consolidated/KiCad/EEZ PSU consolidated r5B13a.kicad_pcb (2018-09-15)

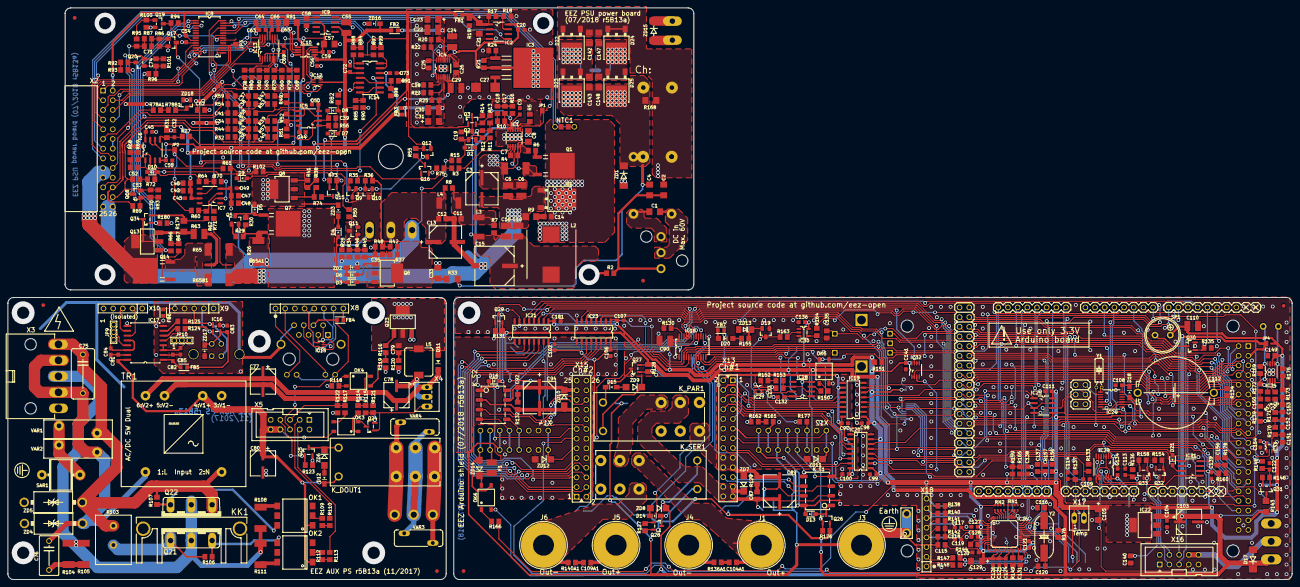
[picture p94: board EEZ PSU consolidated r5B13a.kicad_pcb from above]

Board: 2 copper layers, 337.0 x 150.0 mm, 546 parts (0 on the bottom side), 428 nets.

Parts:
C1, C2, C4: 4n7/100V; C1206
C3, C86, C96: 50SVPF18M; CAPAE830X650N
C5, C6: 4u7/100V; C1210
C7, C87, C92, C150, C153: 470n; C0805
C8, C33: 1u/100V; C1206
C9, C20, C32, C43, C44, C45, C49, C50, C51, C54, C56, C59, C63, C65, C69, C72, C73, C81, C82, C83, C84, C85, C97, C98, C99, C100, C101, C102, C104, C106, C107, C108, C109, C111, C113, C114, C121, C122, C123, C124, C125, C126, C127, C128, C132, C134, C136, C139, C141, C154: 100n; C0603
C10, C16, C22, C24, C29, C30, C55, C90, C110: 10u; C1210
C11, C26, C46, C48, C58, C64, C66, C104A1, C109A1, C149, C156: 1u; C0805
C12: n.c.; C0805
C13: EEEFK1H470P; CAPAE830X1050N
C14, C19: 470p; C0805
C15: EEEFK1J101P; PANASONIC_F
C17, C39: 120p; C0805
C18, C151, C152: 4n7; C0805
C21, C57, C130: 4u7; EC1206
C23, C31, C105, C129: 10u; EC1206
C25, C28, C35, C42, C47, C62, C70, C74, C118, C131, C135, C137, C138: 10n; C0805
C27: 1uF/50V Tant.; C_6032-28R
C34, C41: 47p; C0805
C36, C37, C38, C40, C71: 2n2; C0805
C52, C53: 1n; C0805
C60, C61, C67, C68: 3n3; C0805
C75: 6n8 (X1); C102-064X133
C76: 47n/400V; C075-052X106
C77, C80, C103: 47u; CAPAE660X610N
C78: 220u; CAPAE660X610N
C79, C133, C140: 47n; C0805
C88, C91, C93, C95: 4n7/100V; C1210
C89, C94: UWT1H220MCL; CAPAE830X650N
C112: EECS5R5H105; SG-R20MM
C115: 22n; C0805
C116, C120: 18p; C0805
C117, C119: 6n8; C0603
C142, C143, C147, C148: 1n; C1206
C144: n.c; C1206
C145, C146: 2m2; ECAP7.5_18
C155: 220n; C0805
D1, D22, D23, D24, D25: STPS15H100; TO252
D2, D3, D4, D5, D6, D7, D8, D9, D10, D13, D16, D21: BAS316; SOD323-R
D11, D20: SKL16; SOD123
D12, D14, D15, D18: BAS316; SOD323-W
D17: SMBJ5.0A-TR; DO214AA
D19: BAT54S; SOT23
F1: 50mA; F1210
FB1, FB2, FB3, FB4, FB5, FB6, FB7: 60R@100MHz; BEAD0603
FM1, FM2, FM3, FM4, FM5, FM6: FIDUCIAL_2; FIDUCIAL_DUAL
IC1: LTC3864EMSE#PBF; LTC_05-08-1666
IC2: LP2951SO8; SOIC127P600X175-8N
IC3: TL783CKTTR; TO254P1524X483-4N
IC4: LTC3260EMSE#PBF; SOP50P490X110-17N
IC5, IC6: TL072D; SOIC127P600X173-8N
IC7: LTC2050HVCS8#PBF; SOIC127P600X173-8N
IC8: MCP23S17-E/SS; SOP65P780X200-28N
IC9: REF5025AIDG4; SOIC127P600X175-8N
IC10: DAC8552IDGKTG4; DGK8-M
IC12: TS5A9411DCKT; SOT65P210X110-6N
IC13: ADS1120IPWR; PW(R-PDSO-G16)
IC14: LP339D; SOIC127P600X175-14N
IC15: TPD4E002DRL; DRL5
IC16: TPD2E001DZDR; SOP192P292X122-4N
IC17: ADUM3160BRWZ; SOIC-16W
IC18: TLC5925IDBQR; SOP63P600X175-24N
IC19, IC23: Si8641EC-B-IS1; SOIC-16
IC20, IC21: SI8651EC-B-IS1; SOIC-16
IC22: LD1117ADT33TR; SOT223
IC24: PCA21125T/Q900/1,1; SOP65P640X120-14N
IC25: AT25256B-SSHL-B; SOIC127P600X175-8N
IC26: W5500; TQFP48-7X7
IC27: BC857BS; SOT65P210X110-6N
IC28: TLC555; SOIC127P600X175-8N
IC29: SN74LVC08APWR; SOP65P640X120-14N
IC30: SN74LV1T34DBVR; SOT95P280X145-5N
IC31: TPS3705-33D; SOIC127P600X175-8N
IC32: SN74LVC2G02DCTR; SOP65P400X130-8N
IC33: 74LVC1G125GW.125; SOT65P210X110-5N
IC34: TPA6205A1DGN; SOP65P490X110-9N
J1, J5: BS-244DSM-R; BP_5_12
J2: 1-726388-2; PCB_TAB-4.8MM
J3: BS-244DSM-G; BP_5_12
J4, J6: BS-244DSM-B; BP_5_12
J7: 693072010801
JP1, JP2, JP3, JP4: JP3-CUT
JP9, JP10: ZL303-03P
KK1: SK 145/37,5; SK145
K_DOUT1: RT424005; RT-C_016A5_ROUND
K_PAR1: RT424005; RT-C_016A5_ROUND
K_S1, K_S2: G6K-2F-5DC; G6K-2F
K_SER1: RT424005; RT-C_016A5_ROUND
L1: RN112-4-02; RN112
L2: 7443551331; WE-HCI_1350_1365
L3, L4: IHLP2020CZER3R3M11; IHLP-2020BZ-11
L5: 470u; DE0704
LCD1: TFT_320QVT; LCD_TFT_9341_MIRROR
LED_CC1, LED_CC2: HSMH-C170; LED_HSMH-C170
LED_CV1, LED_CV2: HSMY-C170; LED_0805
LED_O1, LED_O2: HSMG-C170; LED_0805
LED_PROG1, LED_PROG2: HSMH-C170; LED_HSMH-C170
LED_PWR1: HSMD-C170; LED_0805
LED_S1, LED_S2: HSMY-C170; LED_0805
LED_SP1: HSMH-C170; LED_HSMH-C170
MCU1: Arduino Due; ARDUINO+ICSP_MIRROR
NTC1: 10K/Beta:3570K; R_0204_5+0805
OK1: MOC3052; DIL6-SMD
OK2: MOC3062; DIL6-SMD
OK3, OK4, OK5, OK6: HCPL-181
Q1, Q7: IRFR5305; TO229P990X239-3N
Q2, Q9, Q10, Q18: MMBT5401; SOT23-BEC
Q3, Q16, Q24, Q25, Q30, Q32, Q33, Q34: 2N7002; SOT103P240X110-3N
Q4: IRFP250N; TO247BH-CLR
Q5: BC857C; SOT23-BEC
Q6, Q8: BCP56-16.115; SOT230P700X180-4N
Q11, Q12, Q17, Q19, Q20: MMBT5551; SOT23-BEC
Q13, Q23: IRLL2705PBF; SOT223
Q14: IRFR48ZPBF; TO229P990X239-3N
Q15, Q26, Q27, Q28, Q29, Q31: IRLML2246TRPBF; SOT95P237X112-3N
Q21, Q22: BTA26-600; TOP3S-1
R2, R14, R32, R59: n.c.; R0805
R3, R10, R11, R19, R27, R40, R49, R51, R58, R64, R69, R72, R74, R82, R91, R94, R95, R98, R102, R121, R122, R139, R145, R149, R157, R165, R172, R173: 10K; R0805
R4: R010/2W; R2512
R5, R66, R67, R85, R86, R87, R100, R154, R158, R174, R180: 47K; R0805
R6, R129, R132, R136A1, R140A1: 1R; R0805
R7, R8, R42, R116, R155: 100R; R0805
R9, R33, R81, R143: 10R; R1206
R12, R15, R22, R23, R73, R75, R123, R135, R146, R160, R178: 100K; R0805
R13, R20, R25: 316K; R0805
R16, R126, R127, R128, R131, R133, R136, R137, R156, R159, R161, R162: 4K7; R0805
R17, R34: 16K; R0805
R18, R84, R97: 5K1; R0805
R21, R31, R35, R36, R41, R47, R57, R76, R77, R79, R80, R110, R113, R118, R166, R177: 220R; R0805
R24, R55, R130, R151: 1K8; R0805
R26: 2R2/2W; R2512
R28, R38, R68, R92, R114, R120, R163, R164, R170, R171: 1K; R0805
R29, R30, R45, R61, R90, R93, R106, R107, R119: 2K2; R0805
R37, R50, R78A1, R78B1: 470R; R0805
R39, R52: 7K5 0.1%; R0805
R43, R53: 100K 0.1%; R0805
R44, R54: 24K 0.1%; R0805
R46, R89, R96, R152, R153: 750R; R0805
R48: 51K; R0805
R56: 0R; R0805
R60, R70: 3K9 0.1%; R0805
R62, R71: 82R 0.1%; R0805
R63: 0R082; R1210
R65, R65B1: 0R030; R2512
R65A1: 0R030; R_2512-4WIRE
R83, R101: 330R; R0805
R88, R99, R115, R117: 5K6; R0805
R103: 18-22R/7W; R_0913
R104, R105, R108, R111: 330R/2W; R2512
R109, R112, R138, R140, R141, R142: 49R9; R0805
R124, R125: 22R; R0805
R134, R147, R148, R150: 180R; R0805
R144: 12K4; R0805
R167: n.c.; R1206
R168: 12K; R1206
R169, R175: 20K; R0805
R176: 1M; R0805
R179: 0R75; R1206
RN1, RN2: 4x10K; CAY16
SAR1: CG2-470L; SAR
SP1, SP2: LD-BZEN-0903
SW1: A101SYCQ04; M9040P
SW2: PEC12R-4225F-S0024; EC12E_SW
SW3: 1301.9316; TACTM-6XN
TR1: VTX-214-005-0512; PCB_ACDC_VTX_5W_DUAL
VAR1, VAR2: ERZE14A431; VARISTOR
VAR3, VAR4: ERZE11A431; VARISTOR_13MM
X1: 39-30-1039; MINIFIT_39301039
X2: SSW-113-02-T-D-RA
X3: 39303055; MINIFIT_6659-5
X4: 22-23-2031
X5, X16: 09185067324; IDC-10PIN
X6: CTB9300/3A + CTB92VG/3S; WR-TBL_3-PIN
X7: Amphenol: LMJ2138812S0LOT6C or WE: 74990101210; RJ45-VERT
X8: 826629-8; HEADER_8-PIN
X9, X10: 826629-5; SSW-105-02-S-S
X11: 2411-01; KUSBVX-BS1N
X12, X14: MC000006; MC000006_MIRROR
X13, X15: TSW-113-07-F-D
X17: 22-23-2021
X18: MC34753; HEADER_8-PIN
X19: 282836-2; TBLOCK5.0_2
X20: PCA-6B-20-HL-3 or 52746-2071; FPC-20_ROTATED
Y1: 32.768kHz; R26_XTAL
Y2: 25MHz; HC-49_4H
ZD1: SMAJ51A; DO214AA
ZD2: BZX384-C15; SOD323-W
ZD3: PDZ6.2B; SOD323-W
ZD4, ZD5: 1.5KE400CA; DO201-BIDIR
ZD6, ZD8, ZD9, ZD11, ZD12, ZD14: SMAJ18A; DO214AC
ZD7, ZD10: P4SMAJ48A; DO214AC
ZD13: 4V3; MINIMELF
ZD15: n.c.; DO214AA
ZD16, ZD17: PDZ5.6B; SOD323-W
ZD18: SLVU2.8-TP; SOT23

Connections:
0V: C77.2, Q23.3, Q24.2, R119.1, R120.1, R121.2, TR1.5
+3V3: C90.1, C98.1, C99.1, C101.1, C105.+, C107.1, C110.2, C111.1, C115.1, C121.2, C123.1, C124.1, C125.1, C126.1, C127.1, C128.1, C129.+, C134.2, C136.1, C139.2, C141.1, C149.2, C154.2, D18.A, IC18.24, IC19.1, IC20.1, IC20.7, IC21.1, IC21.7, IC22.4, IC23.1, IC25.3, IC25.7, IC25.8, IC26.4, IC26.8, IC26.11, IC26.15, IC26.17, IC26.21, IC26.28, IC29.14, IC30.5, IC31.2, IC32.8, IC33.5, IC34.6, J7.4, JP4.NO, Q31.2, R138.1, R139.2, R140.2, R146.2, R151.1, R156.1, R159.1, RN2.6, RN2.7, RN2.8, SP1.+B, X13.15, X15.15, X17.1, X18.8, X20.1, X20.17, X20.18
+5V: C54.1, C63.2, C64.2, C80.1, C81.1, C103.1, C104.1, D12.C, D17.C, FB1.P$2, FB7.P$1, IC8.9, IC13.13, IC17.16, IC22.3, JP4.NC, K_DOUT1.A1, LED_CC1.A, LED_CC2.A, LED_CV1.A, LED_CV2.A, LED_O1.A, LED_O2.A, LED_PROG1.A, LED_PROG2.A, LED_PWR1.A, LED_S1.A, LED_S2.A, LED_SP1.A, MCU1.5V, OK1.1, OK2.1, OK3.4, Q12.B, Q15.2, Q26.2, Q27.2, Q28.2, Q29.2, R73.1, R84.2, R94.2, R97.2, R126.2, R127.2, R128.2, R131.2, SW1.3, TR1.4, X2.2, X5.8, X5.10
+VREF: C57.+, C59.2, C69.2, IC9.6, IC10.2, IC13.9, R27.1
-12V: C29.1, IC4.6, R38.2, R41.2
/AC soft-start, +5V power/+12VDC: C77.1, C78.1, D11.C, OK4.4, R114.1, R115.1, TR1.6, X4.1
/AC soft-start, +5V power/AUX_FAN_CTRL: OK4.1, X5.6
/AC soft-start, +5V power/AUX_FAN_SENSE: R117.2, R122.1, X5.5
/AC soft-start, +5V power/AUX_PWR_DIRECT: R110.2, X5.3
/AC soft-start, +5V power/AUX_PWR_SSTART: R113.2, X5.4
/Bias power/-5VOUT: C30.2, C31.-, FB3.P$1, IC4.5, R25.2
/Binding posts relays, LED driver/OUT1+: C86.1, C104A1.1, J1.P$1, K_SER1.12B
/Binding posts relays, LED driver/OUT1-: C86.2, C89.2, C91.2, J4.P$1, K_PAR1.14B, K_S1.7, R129.1, R136A1.1, X13.17, X13.18, X13.19, X13.20, ZD7.A
/Binding posts relays, LED driver/OUT2+: C92.1, C93.1, C94.1, C96.1, C109A1.1, J5.P$1, K_PAR1.14A, K_S2.7, X15.23, X15.24, X15.25, X15.26, ZD10.C
/Binding posts relays, LED driver/OUT2-: C96.2, J6.P$1, K_SER1.12A, R140A1.1
/Binding posts relays, LED driver/PWR_IN1+: C87.1, C88.1, C89.1, K_PAR1.11A, K_S1.2, X13.23, X13.24, X13.25, X13.26, ZD7.C
/Binding posts relays, LED driver/PWR_IN2-: C94.2, C95.2, K_PAR1.11B, K_S2.2, R132.1, X15.17, X15.18, X15.19, X15.20, ZD10.A
/Binding posts relays, LED driver/SENSE1+: K_S1.4, X12.5, X12.5.1
/Binding posts relays, LED driver/SENSE1-: K_S1.5, X12.4, X12.4.1
/Binding posts relays, LED driver/SENSE2+: K_S2.5, X14.5, X14.5.1
/Binding posts relays, LED driver/SENSE2-: K_S2.4, X14.4, X14.4.1
/Digital control, voltage reference/AUX_USET_IN: R78A1.2, X2.11
/Digital control, voltage reference/AUX_USET_SW: IC8.25, IC12.1
/Digital control, voltage reference/CS_ADC: IC13.2, X2.6
/Digital control, voltage reference/CS_DAC: IC10.5, X2.4
/Digital control, voltage reference/CS_EXPANDER: IC8.11, X2.3
/Digital control, voltage reference/PS_MISO: IC8.14, IC13.15, X2.9
/Digital control, voltage reference/PS_MOSI: IC8.13, IC10.7, IC13.16, X2.1
/Digital control, voltage reference/PS_SCLK: IC8.12, IC10.6, IC13.1, X2.7
/Digital control, voltage reference/U_SET: IC10.4, IC12.4
/Digital control, voltage reference/~INT: JP3.COM, X2.8
/Digital control, voltage reference/~PS_DRDY: IC13.14, JP3.NC
/Digital control, voltage reference/~PS_RESET: IC8.18, X2.5
/Digital control, voltage reference/~SET_DP: IC8.22, Q15.1, R73.2
/EEZ PSU consolidated r5B13a_12/AC_IN1: C147.1, C148.2, D24.3, D25.1, D25.2, R167.2, X19.1, ZD15.A
/EEZ PSU consolidated r5B13a_12/AC_IN2: C142.1, C143.2, C144.1, D22.3, D23.1, D23.2, X19.2, ZD15.C
/EEZ PSU consolidated r5B13a_12/AUDIO_OUT: IC33.2, X20.10
/Ethernet, USB, Fan/AUX_+3V3: FB4.P$2, X8.8
/Ethernet, USB, Fan/AUX_ETH_ACTLED: X7.10, X8.2
/Ethernet, USB, Fan/AUX_ETH_IN+: IC15.4, X7.3, X8.4
/Ethernet, USB, Fan/AUX_ETH_IN-: IC15.5, X7.6, X8.5
/Ethernet, USB, Fan/AUX_ETH_LINKLED: X7.12, X8.1
/Ethernet, USB, Fan/AUX_ETH_OUT+: IC15.3, X7.2, X8.6
/Ethernet, USB, Fan/AUX_ETH_OUT-: IC15.1, X7.1, X8.7
/Ethernet, USB, Fan/D+: IC16.2, R125.1, X9.3, X11.3
/Ethernet, USB, Fan/D-: IC16.3, R124.1, X9.2, X11.2
/Ethernet, USB, Fan/XUSB_GND: C82.2, C83.1, C85.2, FB6.P$2, IC16.1, IC17.2, IC17.8, JP10.3, X9.4, X11.4, ZD17.A
/Ethernet, USB, Fan/XUSB_VBUS: C83.2, FB5.P$1, IC16.4, X11.1, ZD17.C
/Isolators, Arduino/CH1_MISO: IC19.11, X13.9
/Isolators, Arduino/CH1_MOSI: IC19.14, X13.1
/Isolators, Arduino/CH1_SCLK: IC20.12, X13.7
/Isolators, Arduino/CH1_SYNC: IC20.15, X13.16
/Isolators, Arduino/CH2_MISO: IC23.11, X15.9
/Isolators, Arduino/CH2_MOSI: IC21.14, X15.1
/Isolators, Arduino/CH2_SCLK: IC23.12, X15.7
/Isolators, Arduino/CH2_SYNC: IC21.15, X15.16
/Isolators, Arduino/CH2_VDD: C102.1, C106.1, IC21.10, IC21.16, IC23.10, IC23.16, X15.2
/Isolators, Arduino/FAN_PWM: MCU1.6, X16.6
/Isolators, Arduino/FAN_SENSE: MCU1.13, X16.5
/Isolators, Arduino/ISOLATOR1_EN: IC19.7, MCU1.14
/Isolators, Arduino/ISOLATOR2_EN: IC23.7, MCU1.45
/Isolators, Arduino/~ADC1_SELECT: IC20.4, MCU1.15
/Isolators, Arduino/~ADC2_SELECT: IC23.4, MCU1.48
/Isolators, Arduino/~CH1_ADC: IC20.13, X13.6
/Isolators, Arduino/~CH1_DAC: IC19.12, X13.4
/Isolators, Arduino/~CH1_EXPANDER: IC19.13, X13.3
/Isolators, Arduino/~CH1_INT: IC20.11, X13.8
/Isolators, Arduino/~CH1_RESET: IC20.14, X13.5
/Isolators, Arduino/~CH2_ADC: IC23.13, X15.6
/Isolators, Arduino/~CH2_DAC: IC21.12, X15.4
/Isolators, Arduino/~CH2_EXPANDER: IC21.13, X15.3
/Isolators, Arduino/~CH2_INT: IC21.11, X15.8
/Isolators, Arduino/~CH2_RESET: IC23.14, X15.5
/Isolators, Arduino/~CONVEND1: IC20.6, MCU1.21
/Isolators, Arduino/~CONVEND2: IC21.6, MCU1.20
/Isolators, Arduino/~DAC1_SELECT: IC19.5, MCU1.16
/Isolators, Arduino/~DAC2_SELECT: IC21.5, MCU1.47
/Isolators, Arduino/~IO_EXPANDER1: IC19.4, MCU1.17
/Isolators, Arduino/~IO_EXPANDER2: IC21.4, MCU1.46
/Post-regulator/GCOM: JP2.COM, R39.1, R60.1
/Post-regulator/ISENSE+: IC7.3, R60.2, R62.2
/Post-regulator/ISENSE-: IC7.2, R70.1, R71.2
/Power pre-regulator/DC+: C1.2, L1.3, X1.3
/Power pre-regulator/DC-: C1.1, L1.1, X1.2
/Power pre-regulator/FB: IC1.5, Q3.2, R13.2, R14.2, R16.1
/Power pre-regulator/MCU_VCC: NTC1.2, NTC1.2.1, X2.15
/Power pre-regulator/SGND: C9.1, C17.2, C18.2, IC1.3, JP1.NO, R5.2, R16.2
/Power pre-regulator/SYNC: JP1.NC, X2.16
/Power pre-regulator/TEMP_NTC: NTC1.1, NTC1.1.1, X2.13
/Reset, load temp, digital input/AUX1_USET_IN: X12.8, X12.8.1, X13.11, ZD11.C
/Reset, load temp, digital input/AUX2_USET_IN: X14.8, X14.8.1, X15.11, ZD12.C
/Reset, load temp, digital input/NTC_IN: R177.1, X12.6, X12.6.1
/Reset, load temp, digital input/TEMP_FREQ1: IC28.3, R150.1
/Reset, load temp, digital input/~RST_OUT: IC29.3, IC29.4, IC29.9, IC29.13
/SPI peripherals, TFT display/1V2O: C131.2, IC26.22
/SPI peripherals, TFT display/ETH_ACTLED: IC26.27, R147.1
/SPI peripherals, TFT display/ETH_IN+: C119.1, R142.1, X18.4
/SPI peripherals, TFT display/ETH_IN-: C117.1, R141.2, X18.5
/SPI peripherals, TFT display/ETH_LINKLED: IC26.25, R148.1
/SPI peripherals, TFT display/ETH_OUT+: IC26.2, R140.1, X18.6
/SPI peripherals, TFT display/ETH_OUT-: IC26.1, R138.2, X18.7
/SPI peripherals, TFT display/LCD_RD: LCD1.6, R139.1
AC_EARTH: FB6.P$1, SAR1.P$2, X3.1, X7.8, X7.SH1, X7.SH2, X9.5, X11.M1, X11.M2, ZD4.C, ZD5.C
BATT_NTC: MCU1.A4, OK5.4, R151.2
BP_SELECT: IC18.4, MCU1.9
BUZZER: MCU1.12, Q30.1, R135.2
CC_ACTIVE: IC8.23, R97.1, R99.2
CH1_GND: C97.2, C100.2, C132.2, C133.1, IC19.9, IC19.15, IC20.9, IC28.1, OK5.2, X12.7, X12.7.1, X13.10, X13.12, X13.14, ZD11.A
CH1_VDD: C97.1, C100.1, C132.1, IC19.10, IC19.16, IC20.10, IC20.16, IC27.1, IC27.4, IC28.4, IC28.8, X13.2
CH2_GND: C102.2, C106.2, IC21.9, IC23.9, IC23.15, X14.7, X14.7.1, X15.10, X15.12, X15.14, ZD12.A
CURR_5A: IC8.1, Q14.1, R67.2
CURR_50MA: IC8.3, Q34.1, R180.2
CURR_500MA: IC8.2, Q13.1, R66.2
CV_ACTIVE: IC8.26, R84.1, R88.2
DC_OUT: C3.1, C4.2, C5.1, C6.1, C7.2, C8.1, C27.+, C143.1, C145.+, C146.+, C148.1, D23.3, D25.3, IC1.11, IC3.3, L1.4, R4.1, R33.1, R168.1, ZD1.C
DOUT1: MCU1.A11, R166.1
DOUT2: IC29.5, MCU1.A3
EARTH: C2.2, C4.1, C88.2, C91.1, C93.2, C95.1, C115.2, C118.2, J2.P$1, J2.P$2, J3.P$1, R2.2, X1.1, X12.3, X12.3.1, X14.3, X14.3.1, X18.3
ENC_A: C138.1, MCU1.A9, R165.1
ENC_B: C137.2, MCU1.A8, R157.1
ENC_SW: C135.2, MCU1.A10, SW2.D
EXTSD_CS: J7.2, MCU1.A12
EXT_TRIG: MCU1.A7, R164.1
GND: C2.1, C3.2, C5.2, C6.2, C8.2, C10.2, C16.2, C20.2, C21.-, C22.2, C23.-, C24.2, C25.1, C27.-, C28.1, C29.2, C30.1, C31.+, C32.2, C33.2, C35.2, C42.1, C43.2, C44.1, C45.1, C46.1, C47.1, C48.1, C49.2, C50.1, C51.1, C54.2, C55.2, C56.1, C57.-, C58.2, C59.1, C60.1, C61.2, C62.1, C63.1, C64.1, C65.1, C66.1, C67.1, C68.1, C69.1, C72.1, C73.1, C80.2, C81.2, C84.2, C90.2, C98.2, C99.2, C101.2, C103.2, C104.2, C105.-, C107.2, C108.1, C109.1, C110.1, C111.2, C112.2, C113.1, C114.1, C116.2, C120.2, C121.1, C122.1, C123.2, C124.2, C125.2, C126.2, C127.2, C128.2, C129.-, C131.1, C134.1, C135.1, C136.2, C137.1, C138.2, C139.1, C140.1, C141.2, C142.2, C145.-, C146.-, C147.2, C149.1, C150.2, C151.2, C152.2, C154.1, C155.1, C156.2, D1.1, D1.2, D13.A, D16.A, D17.A, D19.1, D22.1, D22.2, D24.1, D24.2, IC1.TP, IC2.4, IC4.2, IC4.14, IC4.17, IC8.10, IC8.15, IC8.16, IC8.17, IC9.4, IC10.8, IC12.3, IC13.3, IC13.4, IC13.5, IC13.8, IC15.2, IC17.9, IC17.15, IC18.1, IC19.2, IC19.8, IC20.8, IC21.8, IC22.1, IC23.2, IC23.8, IC24.7, IC25.4, IC26.29, IC29.7, IC30.3, IC31.3, IC32.4, IC33.1, IC33.3, IC34.7, IC34.TP, J7.6, J7.Z1, J7.Z2, JP2.NO, JP9.3, K_PAR1.A1, K_S1.8, K_S2.8, K_SER1.A1, L1.2, LCD1.1, MCU1.GND, MCU1.GND1, MCU1.GND2, MCU1.GND3, MCU1.GND4, MCU1.ICSP_GND, OK5.3, OK6.2, Q7.2, Q16.2, Q17.E, Q19.E, Q25.2, Q30.2, Q32.2, Q33.2, R9.1, R18.2, R22.2, R23.1, R24.2, R31.2, R45.1, R46.1, R48.1, R66.1, R67.1, R75.1, R86.1, R90.1, R91.2, R100.1, R118.2, R122.2, R123.1, R130.1, R133.2, R135.1, R136.2, R137.2, R149.1, R154.2, R158.2, R168.2, R174.2, R178.2, R180.1, RN1.5, RN1.6, RN1.7, RN1.8, RN2.5, SW2.C, SW2.E, SW2.GND1, SW2.GND2, SW3.1, SW3.2, SW3.5, TR1.3, X2.10, X2.12, X2.14, X5.1, X5.2, X5.9, X10.4, X12.1, X12.1.1, X16.1, X16.2, X16.9, X20.2, X20.19, X20.20, ZD1.A, ZD8.C, ZD9.C, ZD13.A, ZD16.A, ZD18.1, ZD18.2
GNDA: C130.-, IC26.3, IC26.9, IC26.14, IC26.16, IC26.19, IC26.48, R144.1
I_MON: IC7.6, R64.1, R70.2, R80.1
I_SERVO: C52.2, D9.C, D10.A, IC6.1, R102.1
I_SET: IC10.3, R61.1, R76.1
LCDSD_CS: LCD1.38, MCU1.53, X20.9
LCD_BRIGHTNESS: MCU1.7, R145.1
LCD_CS: LCD1.15, MCU1.39, X20.6
LCD_DB0: LCD1.21, MCU1.37
LCD_DB1: LCD1.22, MCU1.36
LCD_DB2: LCD1.23, MCU1.35
LCD_DB3: LCD1.24, MCU1.34
LCD_DB4: LCD1.25, MCU1.33
LCD_DB5: LCD1.26, MCU1.32
LCD_DB6: LCD1.27, MCU1.31
LCD_DB7: LCD1.28, MCU1.30
LCD_DB8: LCD1.7, MCU1.22
LCD_DB9: LCD1.8, MCU1.23
LCD_DB10: LCD1.9, MCU1.24
LCD_DB11: LCD1.10, MCU1.25
LCD_DB12: LCD1.11, MCU1.26
LCD_DB13: LCD1.12, MCU1.27
LCD_DB14: LCD1.13, MCU1.28
LCD_DB15: LCD1.14, MCU1.29
LCD_RESET: LCD1.17, MCU1.38
LCD_RS: LCD1.4, MCU1.41
LCD_WR: LCD1.5, MCU1.40
MISO: IC19.6, IC23.6, IC24.8, IC25.2, IC26.34, J7.7, LCD1.35, MCU1.ICSP_MISO, X20.4
MOSI: IC18.2, IC19.3, IC21.3, IC24.9, IC25.5, IC26.35, J7.3, LCD1.37, MCU1.ICSP_MOSI, X20.5
NTC1: C109.2, MCU1.A5, R133.1, X13.13
NTC2: C114.2, MCU1.A6, R137.1, X15.13
unnamed: C7.1, IC1.9
unnamed: C9.2, IC1.4
unnamed: C10.1, C15.1, C16.1, L2.2, L3.1, R7.1, R11.1, R12.1, R13.1
unnamed: C11.1, L3.2, L4.1, R7.2, R8.1
unnamed: C14.1, D1.3, L2.1, Q1.2
unnamed: C14.2, R9.2
unnamed: C17.1, IC1.6, R10.2
unnamed: C18.1, R10.1
unnamed: C19.1, Q2.C, Q3.3, R14.1
unnamed: C19.2, D2.A, Q2.B, R12.2, R15.1
unnamed: C20.1, C24.1, IC2.8, IC3.2, IC3.4, IC4.1, IC4.11, IC4.13, R21.1
unnamed: C21.+, FB1.P$1, IC2.1, R17.1, R19.1
unnamed: C22.1, C23.+, FB2.P$1, IC4.12, R20.1
unnamed: C25.2, IC4.16
unnamed: C26.1, IC4.9, IC4.10
unnamed: C26.2, IC4.7, IC4.8
unnamed: C28.2, IC4.3
unnamed: C32.1, IC6.5, R27.2, R31.1
unnamed: C33.1, Q6.2, Q6.4, R33.2, R35.2, R36.2
unnamed: C34.2, R40.1
unnamed: C35.1, R37.1
unnamed: C36.1, R43.2, R44.1
unnamed: C37.2, R47.1
unnamed: C38.1, R53.2, R54.1
unnamed: C39.1, D8.C, IC5.2, R51.2, R57.2
unnamed: C39.2, R56.1
unnamed: C40.2, R57.1
unnamed: C41.2, R58.1
unnamed: C52.1, R68.1
unnamed: C53.2, R72.1
unnamed: C58.1, IC9.5
unnamed: C60.2, IC13.11, R77.2
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

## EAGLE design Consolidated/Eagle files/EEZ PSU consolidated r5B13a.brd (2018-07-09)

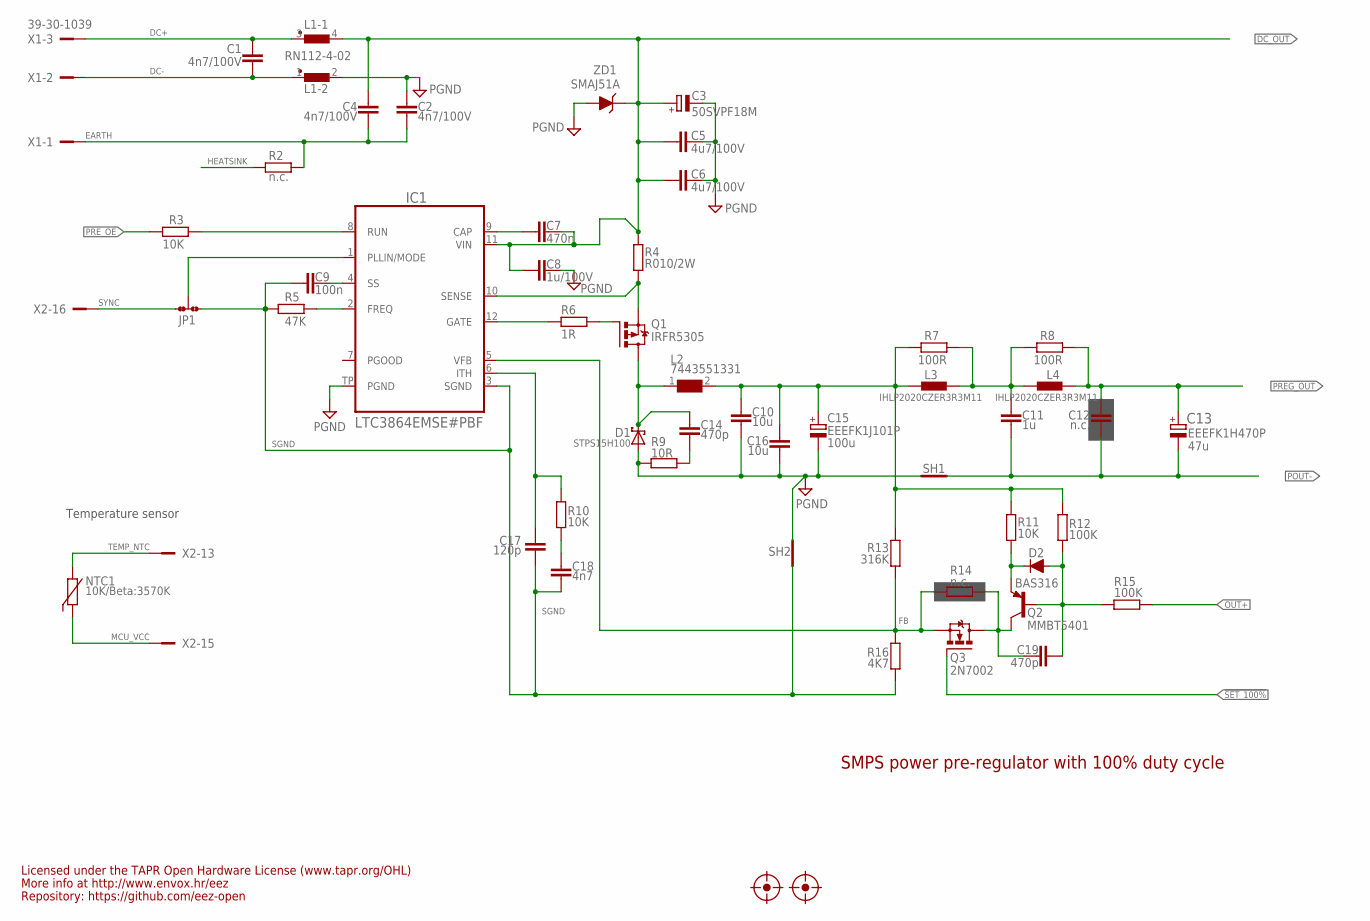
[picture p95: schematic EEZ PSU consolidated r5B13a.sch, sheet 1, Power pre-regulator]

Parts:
C1, C2, C4: 4n7/100V; C1206
C3: 50SVPF18M; CAPAE830X650N; TOLERANCE ±20 %; VOLTAGERATING 63V; MPN EEE-FK1J220P
C5, C6: 4u7/100V; C1210
C7: 470n; C0805
C8: 1u/100V; C1206
C9: 100n; C0603
C10, C16: 10u; C1210
C11: 1u; C0805
C12: n.c.; C0805
C13: EEEFK1H470P; CAPAE830X1050N
C14, C19: 470p; C0805
C15: EEEFK1J101P; PANASONIC_F
C17: 120p; C0805
C18: 4n7; C0805
D1: STPS15H100; TO252
D2: BAS316; SOD323-R
FM1, FM2: FIDUCIAL_2; FIDUCIAL_DUAL
IC1: LTC3864EMSE#PBF; LTC_05-08-1666
JP1: JP3-CUT
L1: RN112-4-02; RN112
L2: 7443551331; WE-HCI_1350/1365
L3, L4: IHLP2020CZER3R3M11; IHLP-2020BZ-11
NTC1: 10K/Beta:3570K; R_0204/5+0805
Q1: IRFR5305; TO229P990X239-3N
Q2: MMBT5401; SOT23-BEC
Q3: 2N7002; SOT103P240X110-3N
R2, R14: n.c.; R0805
R3, R10, R11: 10K; R0805
R4: R010/2W; R2512
R5: 47K; R0805
R6: 1R; R0805
R7, R8: 100R; R0805
R9: 10R; R1206
R12, R15: 100K; R0805
R13: 316K; R0805
R16: 4K7; R0805
SH1: Pgnd to Pout- short; SHORT_NOHOLE
SH2: Sgnd to Pgnd short; SHORT_NOHOLE
X1: 39-30-1039; MINIFIT_39301039
X2: SSW-113-02-T-D-RA; FARNELL 1805583
ZD1: SMAJ51A; DO214AA

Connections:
!SET_100%: Q3.1 (G); also elsewhere on the board
DC+: C1.2, L1.3 (1), X1.3
DC-: C1.1, L1.1, X1.2
DC_OUT: C3.1, C4.2, C5.1, C6.1, C7.2, C8.1, IC1.11 (VIN), L1.4 (2), R4.1, ZD1.C; also elsewhere on the board
EARTH: C2.2, C4.1, R2.2, X1.1; also elsewhere on the board
FB: IC1.5 (VFB), Q3.2 (S), R13.2, R14.2, R16.1
GND: C2.1, C3.2, C5.2, C6.2, C8.2, C10.2, C15.2 (-), C16.2, D1.1 (A), D1.2 (A), IC1.TP (PGND), L1.2, R9.1, SH1.P$2 (GND_B), SH2.P$2 (GND_B), ZD1.A; also elsewhere on the board
HEATSINK: R2.1
L_OUT: C10.1, C15.1 (+), C16.1, L2.2, L3.1, R7.1, R11.1, R12.1, R13.1
MCU_VCC: NTC1.2, NTC1.2.1, X2.15
MODE: IC1.1 (PLLIN/MODE), JP1.COM
unnamed: Q1.1 (G), R6.2
unnamed: D2.C, Q2.E, R11.2
unnamed: C17.1, IC1.6 (ITH), R10.2
unnamed: C18.1, R10.1
unnamed: C7.1, IC1.9 (CAP)
unnamed: IC1.12 (GATE), R6.1
unnamed: IC1.2 (FREQ), R5.1
unnamed: C9.2, IC1.4 (SS)
unnamed: C19.1, Q2.C, Q3.3 (D), R14.1
unnamed: C11.1, L3.2, L4.1, R7.2, R8.1
unnamed: IC1.8 (RUN), R3.1
unnamed: C14.2, R9.2
unnamed: C19.2, D2.A, Q2.B, R12.2, R15.1
OUT+: R15.2; also elsewhere on the board
POUT-: C11.2, C12.2, C13.2, SH1.P$1 (GND_A); also elsewhere on the board
PREG_OUT: C12.1, C13.1, L4.2, R8.2; also elsewhere on the board
PRE_OE: R3.2; also elsewhere on the board
SENSE: IC1.10 (SENSE), Q1.3 (S), R4.2
SGND: C9.1, C17.2, C18.2, IC1.3 (SGND), JP1.NO, R5.2, R16.2, SH2.P$1 (GND_A)
SW: C14.1, D1.3 (C), L2.1, Q1.2 (D)
SYNC: JP1.NC, X2.16
TEMP_NTC: NTC1.1, NTC1.1.1, X2.13

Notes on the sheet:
47u
Licensed under the TAPR Open Hardware License (www.tapr.org/OHL)
Repository: https://github.com/eez-open
More info at http://www.envox.hr/eez
SMPS power pre-regulator with 100% duty cycle
100u
Temperature sensor

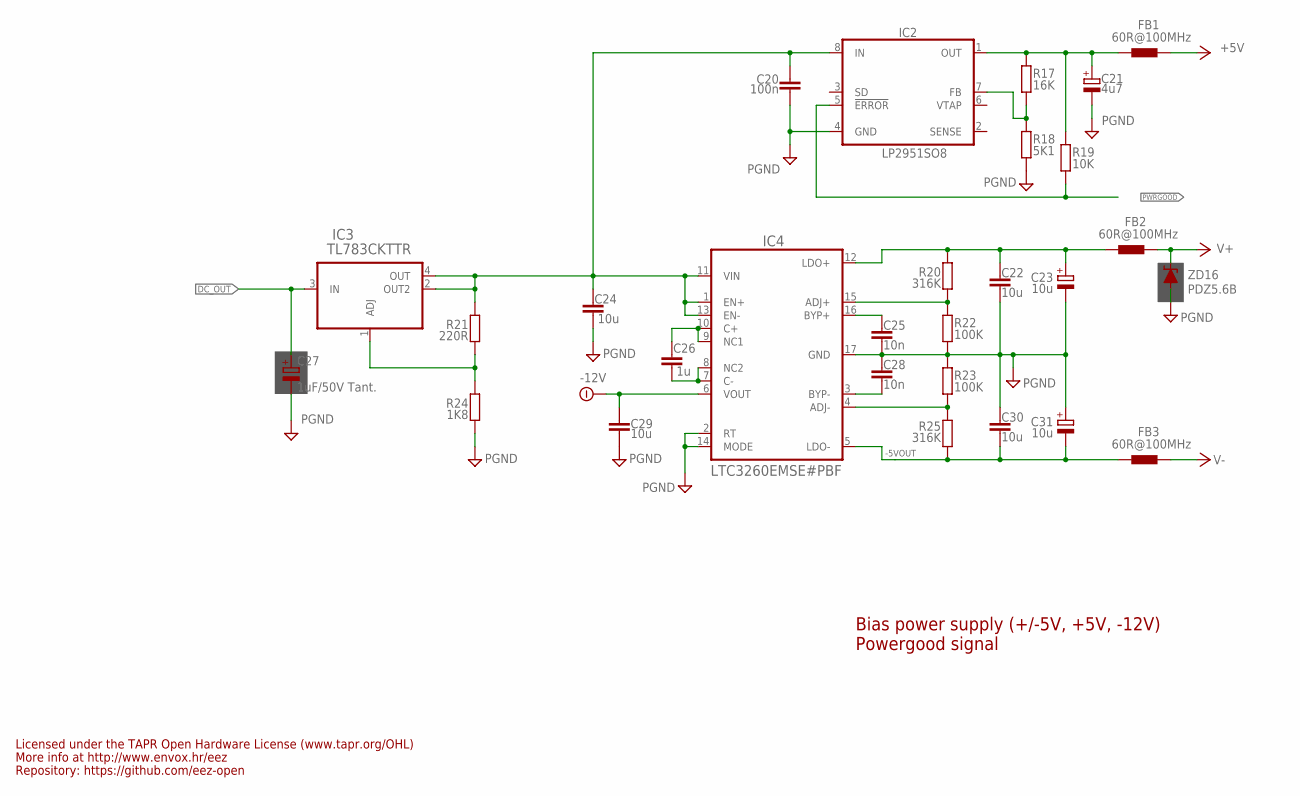
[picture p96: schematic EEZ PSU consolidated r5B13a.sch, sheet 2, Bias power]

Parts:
C20: 100n; C0603
C21: 4u7; EC1206
C22, C24, C29, C30: 10u; C1210
C23, C31: 10u; EC1206
C25, C28: 10n; C0805
C26: 1u; C0805
C27: 1uF/50V Tant.; C/6032-28R
FB1, FB2, FB3: 60R@100MHz; BEAD0603
IC2: LP2951SO8; SOIC127P600X175-8N
IC3: TL783CKTTR; TO254P1524X483-4N
IC4: LTC3260EMSE#PBF; SOP50P490X110-17N
R17: 16K; R0805
R18: 5K1; R0805
R19: 10K; R0805
R20, R25: 316K; R0805
R21: 220R; R0805
R22, R23: 100K; R0805
R24: 1K8; R0805
ZD16: PDZ5.6B; SOD323-W

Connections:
+5V: FB1.P$2 (2); also elsewhere on the board
+VNR: C20.1, C24.1, IC2.8 (IN), IC3.2 (OUT2), IC3.4 (OUT), IC4.1 (EN+), IC4.11 (VIN), IC4.13 (EN-), R21.1
-5VOUT: C30.2, C31.-, FB3.P$1 (1), IC4.5 (LDO-), R25.2
-12V: C29.1, IC4.6 (VOUT); also elsewhere on the board
DC_OUT: C27.+, IC3.3 (IN); also elsewhere on the board
GND: C20.2, C21.-, C22.2, C23.-, C24.2, C25.1, C27.-, C28.1, C29.2, C30.1, C31.+, IC2.4 (GND), IC4.2 (RT), IC4.14 (MODE), IC4.17 (GND), R18.2, R22.2, R23.1, R24.2, ZD16.A; also elsewhere on the board
unnamed: C22.1, C23.+, FB2.P$1 (1), IC4.12 (LDO+), R20.1
unnamed: C26.1, IC4.9 (NC1), IC4.10 (C+)
unnamed: IC3.1 (ADJ), R21.2, R24.1
unnamed: IC4.15 (ADJ+), R20.2, R22.1
unnamed: C26.2, IC4.7 (C-), IC4.8 (NC2)
unnamed: C25.2, IC4.16 (BYP+)
unnamed: IC4.4 (ADJ-), R23.2, R25.1
unnamed: C28.2, IC4.3 (BYP-)
unnamed: IC2.7 (FB), R17.2, R18.1
unnamed: C21.+, FB1.P$1 (1), IC2.1 (OUT), R17.1, R19.1
PWRGOOD: IC2.5 (!ERROR), R19.2; also elsewhere on the board
V+: FB2.P$2 (2), ZD16.C; also elsewhere on the board
V-: FB3.P$2 (2); also elsewhere on the board

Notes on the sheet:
Bias power supply (+/-5V, +5V, -12V)
Licensed under the TAPR Open Hardware License (www.tapr.org/OHL)
Repository: https://github.com/eez-open
More info at http://www.envox.hr/eez
Powergood signal

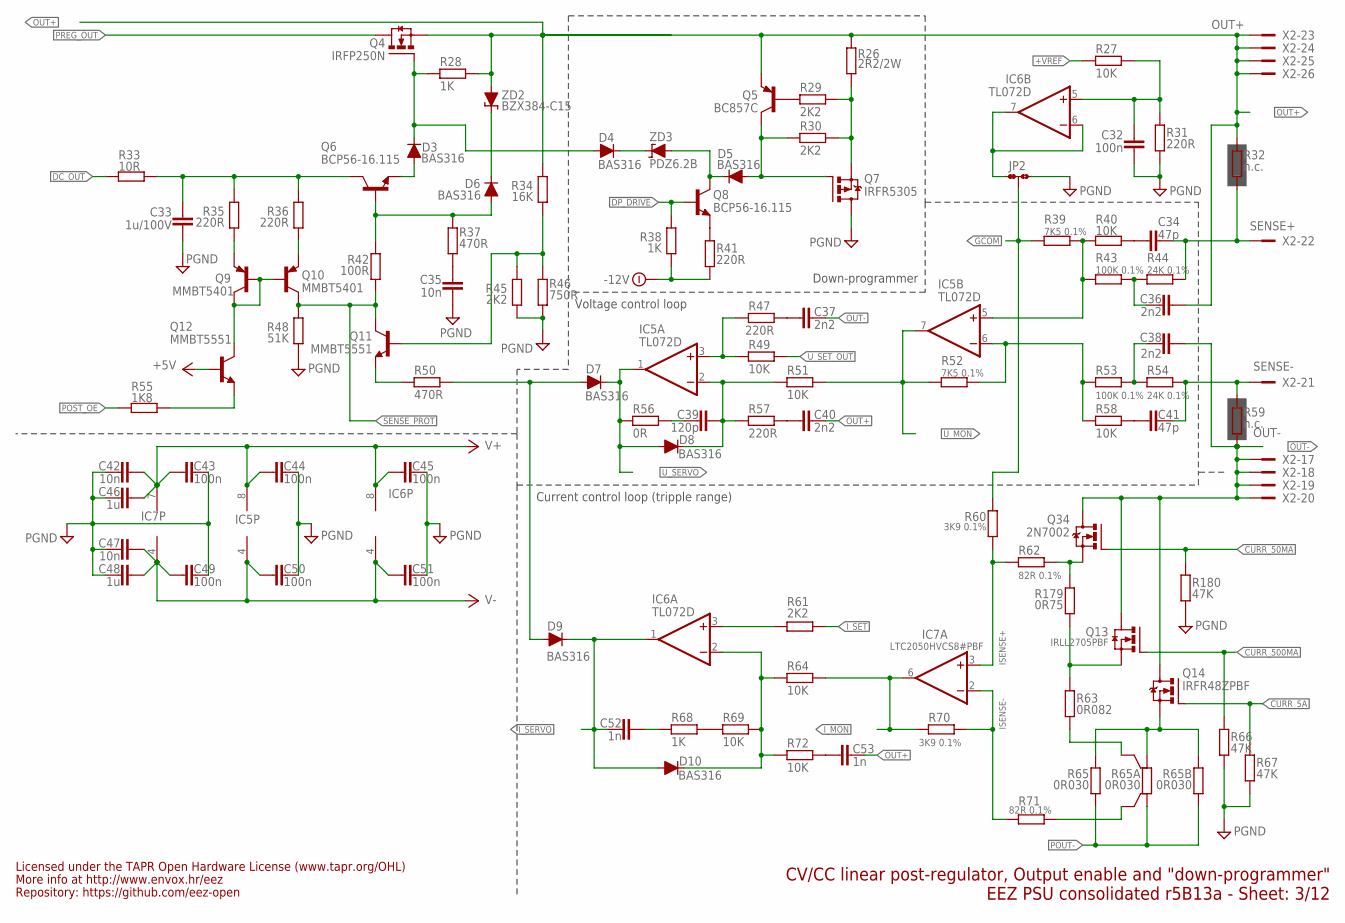
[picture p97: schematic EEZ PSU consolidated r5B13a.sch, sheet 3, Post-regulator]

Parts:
C32, C43, C44, C45, C49, C50, C51: 100n; C0603
C33: 1u/100V; C1206
C34, C41: 47p; C0805
C35, C42, C47: 10n; C0805
C36, C37, C38, C40: 2n2; C0805
C39: 120p; C0805
C46, C48: 1u; C0805
C52, C53: 1n; C0805
D3, D4, D5, D6, D7, D8, D9, D10: BAS316; SOD323-R
IC5, IC6: TL072D; SOIC127P600X173-8N
IC7: LTC2050HVCS8#PBF; SOIC127P600X173-8N
JP2: JP3-CUT
Q4: IRFP250N; TO247BH-CLR
Q5: BC857C; SOT23-BEC
Q6, Q8: BCP56-16.115; SOT230P700X180-4N
Q7: IRFR5305; TO229P990X239-3N
Q9, Q10: MMBT5401; SOT23-BEC
Q11, Q12: MMBT5551; SOT23-BEC
Q13: IRLL2705PBF; SOT223
Q14: IRFR48ZPBF; TO229P990X239-3N
Q34: 2N7002; SOT103P240X110-3N; MPN 2N7002-7-F
R26: 2R2/2W; R2512
R27, R40, R49, R51, R58, R64, R69, R72: 10K; R0805
R28, R38, R68: 1K; R0805
R29, R30, R45, R61: 2K2; R0805
R31, R35, R36, R41, R47, R57: 220R; R0805
R32, R59: n.c.; R0805
R33: 10R; R1206
R34: 16K; R0805
R37, R50: 470R; R0805
R39, R52: 7K5 0.1%; R0805
R42: 100R; R0805
R43, R53: 100K 0.1%; R0805
R44, R54: 24K 0.1%; R0805
R46: 750R; R0805
R48: 51K; R0805
R55: 1K8; R0805
R56: 0R; R0805
R60, R70: 3K9 0.1%; R0805
R62, R71: 82R 0.1%; R0805
R63: 0R082; R1210
R65, R65B: 0R030; R2512
R65A: 0R030; R_2512-4WIRE
R66, R67, R180: 47K; R0805
R179: 0R75; R1206
X2: SSW-113-02-T-D-RA; FARNELL 1805583
ZD2: BZX384-C15; SOD323-W
ZD3: PDZ6.2B; SOD323-W

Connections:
!DP_DRIVE: Q8.1 (B), R38.1; also elsewhere on the board
+5V: Q12.B; also elsewhere on the board
+VREF: R27.1; also elsewhere on the board
-12V: R38.2, R41.2; also elsewhere on the board
CURR_5A: Q14.1 (G), R67.2; also elsewhere on the board
CURR_50MA: Q34.1 (G), R180.2; also elsewhere on the board
CURR_500MA: Q13.1 (G), R66.2; also elsewhere on the board
DC_BIAS: C33.1, Q6.2 (C), Q6.4 (C), R33.2, R35.2, R36.2
DC_OUT: R33.1; also elsewhere on the board
GCOM: JP2.COM, R39.1, R60.1
GND: C32.2, C33.2, C35.2, C42.1, C43.2, C44.1, C45.1, C46.1, C47.1, C48.1, C49.2, C50.1, C51.1, JP2.NO, Q7.2 (D), R31.2, R45.1, R46.1, R48.1, R66.1, R67.1, R180.1; also elsewhere on the board
ISENSE+: IC7.3 (+IN), R60.2, R62.2
ISENSE-: IC7.2 (-IN), R70.1, R71.2
I_MON: IC7.6 (OUT), R64.1, R70.2; also elsewhere on the board
I_SERVO: C52.2, D9.C, D10.A, IC6.1 (OUT); also elsewhere on the board
I_SET: R61.1; also elsewhere on the board
LOOP_CTRL: D7.A, D9.A, R50.1
unnamed: Q8.3 (E), R41.1
unnamed: Q5.B, R29.2
unnamed: C34.2, R40.1
unnamed: C41.2, R58.1
unnamed: C32.1, IC6.5 (+IN), R27.2, R31.1
unnamed: IC6.6 (-IN), IC6.7 (OUT), JP2.NC
unnamed: C38.1, R53.2, R54.1
unnamed: C39.2, R56.1
unnamed: C53.2, R72.1
unnamed: C37.2, R47.1
unnamed: C40.2, R57.1
unnamed: IC5.3 (+IN), R47.2, R49.2
unnamed: C39.1, D8.C, IC5.2 (-IN), R51.2, R57.2
unnamed: D10.C, IC6.2 (-IN), R64.2, R69.2, R72.2
unnamed: Q11.B, R34.1, R45.2, R46.2
unnamed: IC6.3 (+IN), R61.2
unnamed: D3.C, D4.A, Q4.G, R28.1
unnamed: Q34.2 (S), R62.1, R179.1
unnamed: D3.A, Q6.3 (E)
unnamed: D6.A, Q6.1 (B), R37.2, R42.1
unnamed: C35.1, R37.1
unnamed: R63.1, R65A.2S
unnamed: C36.1, R43.2, R44.1
unnamed: D6.C, ZD2.C
unnamed: D4.C, ZD3.C
unnamed: Q11.E, R50.2
unnamed: Q7.3 (S), R26.1, R29.1, R30.1
unnamed: D5.A, Q5.C, Q7.1 (G), R30.2
unnamed: IC5.5 (+IN), R39.2, R40.2, R43.1
unnamed: IC5.6 (-IN), R52.2, R53.1, R58.2
unnamed: R68.2, R69.1
unnamed: C52.1, R68.1
unnamed: Q14.3 (S), R65.2, R65A.2, R65B.2
unnamed: Q10.E, R36.1
unnamed: Q9.E, R35.1
unnamed: Q12.E, R55.2
unnamed: R65A.1S, R71.1
unnamed: Q13.3 (S), R63.2, R179.2
OUT+: C36.2, C40.1, C53.1, Q4.S, Q5.E, R26.2, R28.2, R32.1, R34.2, X2.23, X2.24, X2.25, X2.26, ZD2.A; also elsewhere on the board
OUT-: C37.1, C38.2, Q13.2 (D), Q13.4 (D), Q14.2 (D), Q34.3 (D), R59.2, X2.17, X2.18, X2.19, X2.20; also elsewhere on the board
POST_OE: R55.1; also elsewhere on the board
POUT-: R65.1, R65A.1, R65B.1; also elsewhere on the board
PREG_OUT: Q4.D; also elsewhere on the board
Q7C: Q9.B, Q9.C, Q10.B, Q12.C
Q9C: D5.C, Q8.2 (C), Q8.4 (C), ZD3.A
SENSE+: C34.1, R32.2, R44.2, X2.22; also elsewhere on the board
SENSE-: C41.1, R54.2, R59.1, X2.21; also elsewhere on the board
SENSE_PROT: Q10.C, Q11.C, R42.2, R48.2; also elsewhere on the board
U_MON: IC5.7 (OUT), R51.1, R52.1; also elsewhere on the board
U_SERVO: D7.C, D8.A, IC5.1 (OUT), R56.2; also elsewhere on the board
U_SET_OUT: R49.1; also elsewhere on the board
V+: C42.2, C43.1, C44.2, C45.2, C46.2, IC5.8 (V+), IC6.8 (V+), IC7.7 (V+); also elsewhere on the board
V-: C47.2, C48.2, C49.1, C50.2, C51.2, IC5.4 (V-), IC6.4 (V-), IC7.4 (V-); also elsewhere on the board

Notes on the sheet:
Current control loop (tripple range)
Voltage control loop
CV/CC linear post-regulator, Output enable and "down-programmer"
Down-programmer
Licensed under the TAPR Open Hardware License (www.tapr.org/OHL)
Repository: https://github.com/eez-open
More info at http://www.envox.hr/eez
EEZ PSU consolidated r5B13a - Sheet: 3/12

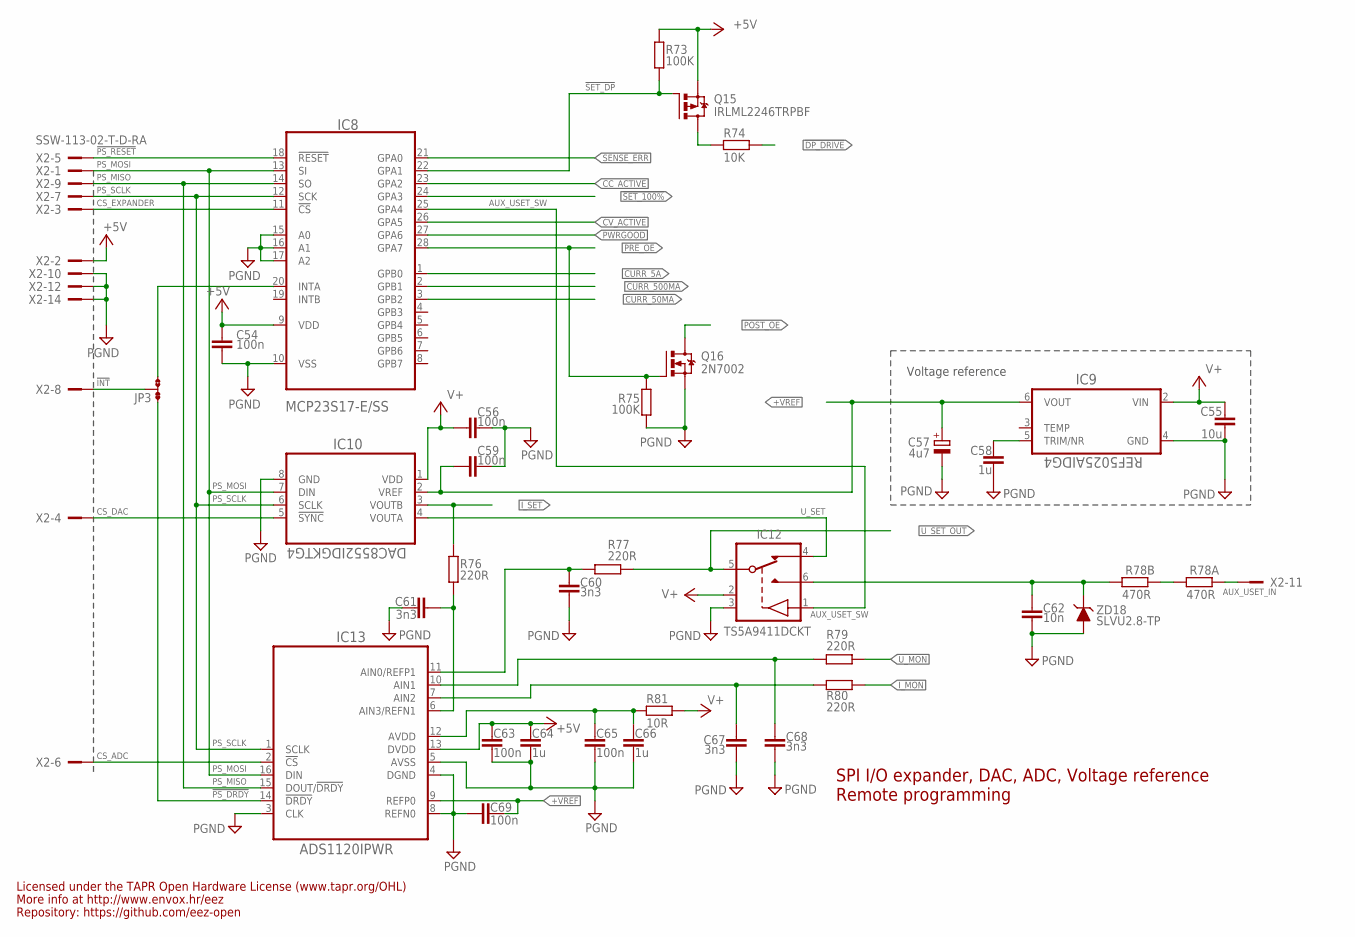
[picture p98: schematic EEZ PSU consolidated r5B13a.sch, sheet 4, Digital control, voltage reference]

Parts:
C54, C56, C59, C63, C65, C69: 100n; C0603
C55: 10u; C1210
C57: 4u7; EC1206
C58, C64, C66: 1u; C0805
C60, C61, C67, C68: 3n3; C0805
C62: 10n; C0805
IC8: MCP23S17-E/SS; SOP65P780X200-28N
IC9: REF5025AIDG4; SOIC127P600X175-8N
IC10: DAC8552IDGKTG4; DGK8-M
IC12: TS5A9411DCKT; SOT65P210X110-6N
IC13: ADS1120IPWR; PW(R-PDSO-G16)
JP3: JP3-CUT
Q15: IRLML2246TRPBF; SOT95P237X112-3N
Q16: 2N7002; SOT103P240X110-3N; MPN 2N7002-7-F
R73, R75: 100K; R0805
R74: 10K; R0805
R76, R77, R79, R80: 220R; R0805
R78A, R78B: 470R; R0805
R81: 10R; R1206
X2: SSW-113-02-T-D-RA; FARNELL 1805583
ZD18: SLVU2.8-TP; SOT23

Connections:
!DP_DRIVE: R74.1; also elsewhere on the board
!INT: JP3.COM, X2.8
!PS_DRDY: IC13.14 (!DRDY), JP3.NC
!PS_RESET: IC8.18 (!RESET), X2.5
!SET_100%: IC8.24 (GPA3); also elsewhere on the board
!SET_DP: IC8.22 (GPA1), Q15.1 (G), R73.2
+5V: C54.1, C63.2, C64.2, IC8.9 (VDD), IC13.13 (DVDD), Q15.2 (S), R73.1, X2.2; also elsewhere on the board
+VREF: C57.+, C59.2, C69.2, IC9.6 (VOUT), IC10.2 (VREF), IC13.9 (REFP0); also elsewhere on the board
AUX_USET_IN: R78A.2, X2.11
AUX_USET_SW: IC8.25 (GPA4), IC12.1 (IN)
CC_ACTIVE: IC8.23 (GPA2); also elsewhere on the board
CS_ADC: IC13.2 (!CS), X2.6
CS_DAC: IC10.5 (!SYNC), X2.4
CS_EXPANDER: IC8.11 (!CS), X2.3
CURR_5A: IC8.1 (GPB0); also elsewhere on the board
CURR_50MA: IC8.3 (GPB2); also elsewhere on the board
CURR_500MA: IC8.2 (GPB1); also elsewhere on the board
CV_ACTIVE: IC8.26 (GPA5); also elsewhere on the board
DP_LED: Q15.3 (D), R74.2
GND: C54.2, C55.2, C56.1, C57.-, C58.2, C59.1, C60.1, C61.2, C62.1, C63.1, C64.1, C65.1, C66.1, C67.1, C68.1, C69.1, IC8.10 (VSS), IC8.15 (A0), IC8.16 (A1), IC8.17 (A2), IC9.4 (GND), IC10.8 (GND), IC12.3 (GND), IC13.3 (CLK), IC13.4 (DGND), IC13.5 (AVSS), IC13.8 (REFN0), Q16.2 (S), R75.1, X2.10, X2.12, X2.14, ZD18.1 (A), ZD18.2 (A); also elsewhere on the board
INT_EXP: IC8.20 (INTA), JP3.NO
I_MON: R80.1; also elsewhere on the board
I_SET: IC10.3 (VOUTB), R76.1; also elsewhere on the board
unnamed: C58.1, IC9.5 (TRIM/NR)
unnamed: C62.2, IC12.6 (S1), R78B.1, ZD18.3 (C)
unnamed: C68.2, IC13.10 (AIN1), R79.2
unnamed: C60.2, IC13.11 (AIN0/REFP1), R77.2
unnamed: C65.2, C66.2, IC13.12 (AVDD), R81.2
unnamed: C61.1, IC13.6 (AIN3/REFN1), R76.2
unnamed: C67.2, IC13.7 (AIN2), R80.2
unnamed: R78A.1, R78B.2
POST_OE: Q16.3 (D); also elsewhere on the board
PRE_OE: IC8.28 (GPA7), Q16.1 (G), R75.2; also elsewhere on the board
PS_MISO: IC8.14 (SO), IC13.15 (DOUT/!DRDY), X2.9
PS_MOSI: IC8.13 (SI), IC10.7 (DIN), IC13.16 (DIN), X2.1
PS_SCLK: IC8.12 (SCK), IC10.6 (SCLK), IC13.1 (SCLK), X2.7
PWRGOOD: IC8.27 (GPA6); also elsewhere on the board
SENSE_ERR: IC8.21 (GPA0); also elsewhere on the board
U_MON: R79.1; also elsewhere on the board
U_SET: IC10.4 (VOUTA), IC12.4 (S2)
U_SET_OUT: IC12.5 (D), R77.1; also elsewhere on the board
V+: C55.1, C56.2, IC9.2 (VIN), IC10.1 (VDD), IC12.2 (VDD), R81.1; also elsewhere on the board

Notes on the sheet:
SPI I/O expander, DAC, ADC, Voltage reference
Voltage reference
Licensed under the TAPR Open Hardware License (www.tapr.org/OHL)
Repository: https://github.com/eez-open
More info at http://www.envox.hr/eez
Remote programming

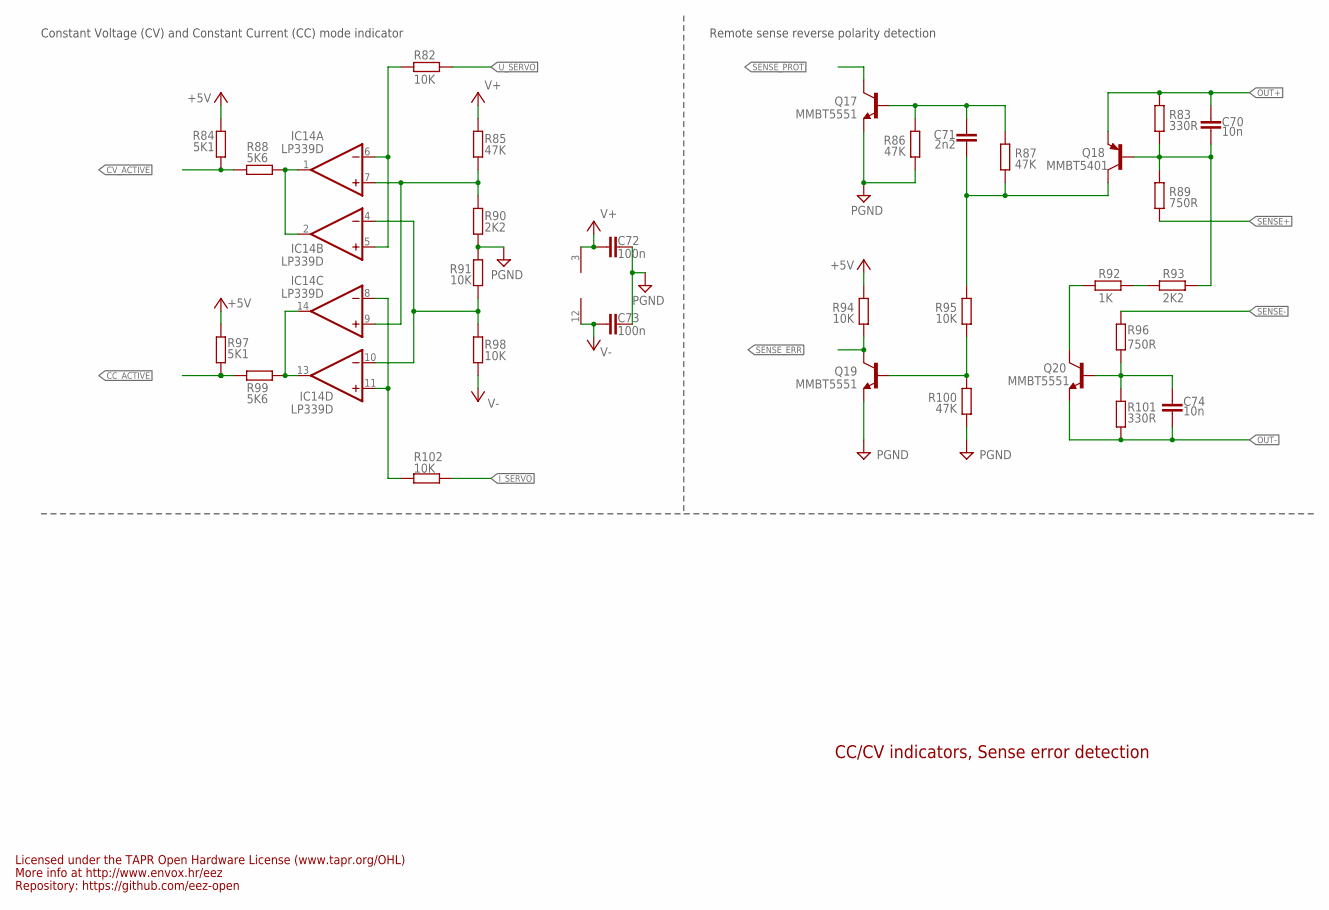
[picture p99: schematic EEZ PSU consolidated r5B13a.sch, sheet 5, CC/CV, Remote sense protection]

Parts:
C70, C74: 10n; C0805
C71: 2n2; C0805
C72, C73: 100n; C0603
IC14: LP339D; SOIC127P600X175-14N
Q17, Q19, Q20: MMBT5551; SOT23-BEC
Q18: MMBT5401; SOT23-BEC
R82, R91, R94, R95, R98, R102: 10K; R0805
R83, R101: 330R; R0805
R84, R97: 5K1; R0805
R85, R86, R87, R100: 47K; R0805
R88, R99: 5K6; R0805
R89, R96: 750R; R0805
R90, R93: 2K2; R0805
R92: 1K; R0805

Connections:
+5V: R84.2, R94.2, R97.2; also elsewhere on the board
CC_ACTIVE: R97.1, R99.2; also elsewhere on the board
CV_ACTIVE: R84.1, R88.2; also elsewhere on the board
GND: C72.1, C73.1, Q17.E, Q19.E, R86.1, R90.1, R91.2, R100.1; also elsewhere on the board
I_SERVO: R102.1; also elsewhere on the board
unnamed: C70.2, Q18.B, R83.1, R89.2, R93.2
unnamed: Q19.B, R95.1, R100.2
unnamed: C71.2, Q18.C, R87.1, R95.2
unnamed: IC14.1 (OUT), IC14.2 (OUT), R88.1
unnamed: Q20.C, R92.1
unnamed: IC14.13 (OUT), IC14.14 (OUT), R99.1
unnamed: C74.1, Q20.B, R96.1, R101.2
unnamed: C71.1, Q17.B, R86.2, R87.2
unnamed: IC14.5 (+IN), IC14.6 (-IN), R82.2
unnamed: IC14.8 (-IN), IC14.11 (+IN), R102.2
unnamed: IC14.7 (+IN), IC14.9 (+IN), R85.1, R90.2
unnamed: R92.2, R93.1
unnamed: IC14.4 (-IN), IC14.10 (-IN), R91.1, R98.2
OUT+: C70.1, Q18.E, R83.2; also elsewhere on the board
OUT-: C74.2, Q20.E, R101.1; also elsewhere on the board
SENSE+: R89.1; also elsewhere on the board
SENSE-: R96.2; also elsewhere on the board
SENSE_ERR: Q19.C, R94.1; also elsewhere on the board
SENSE_PROT: Q17.C; also elsewhere on the board
U_SERVO: R82.1; also elsewhere on the board
V+: C72.2, IC14.3 (V+), R85.2; also elsewhere on the board
V-: C73.2, IC14.12 (GND), R98.1; also elsewhere on the board

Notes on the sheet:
Constant Voltage (CV) and Constant Current (CC) mode indicator
CC/CV indicators, Sense error detection
Licensed under the TAPR Open Hardware License (www.tapr.org/OHL)
Repository: https://github.com/eez-open
More info at http://www.envox.hr/eez
Remote sense reverse polarity detection

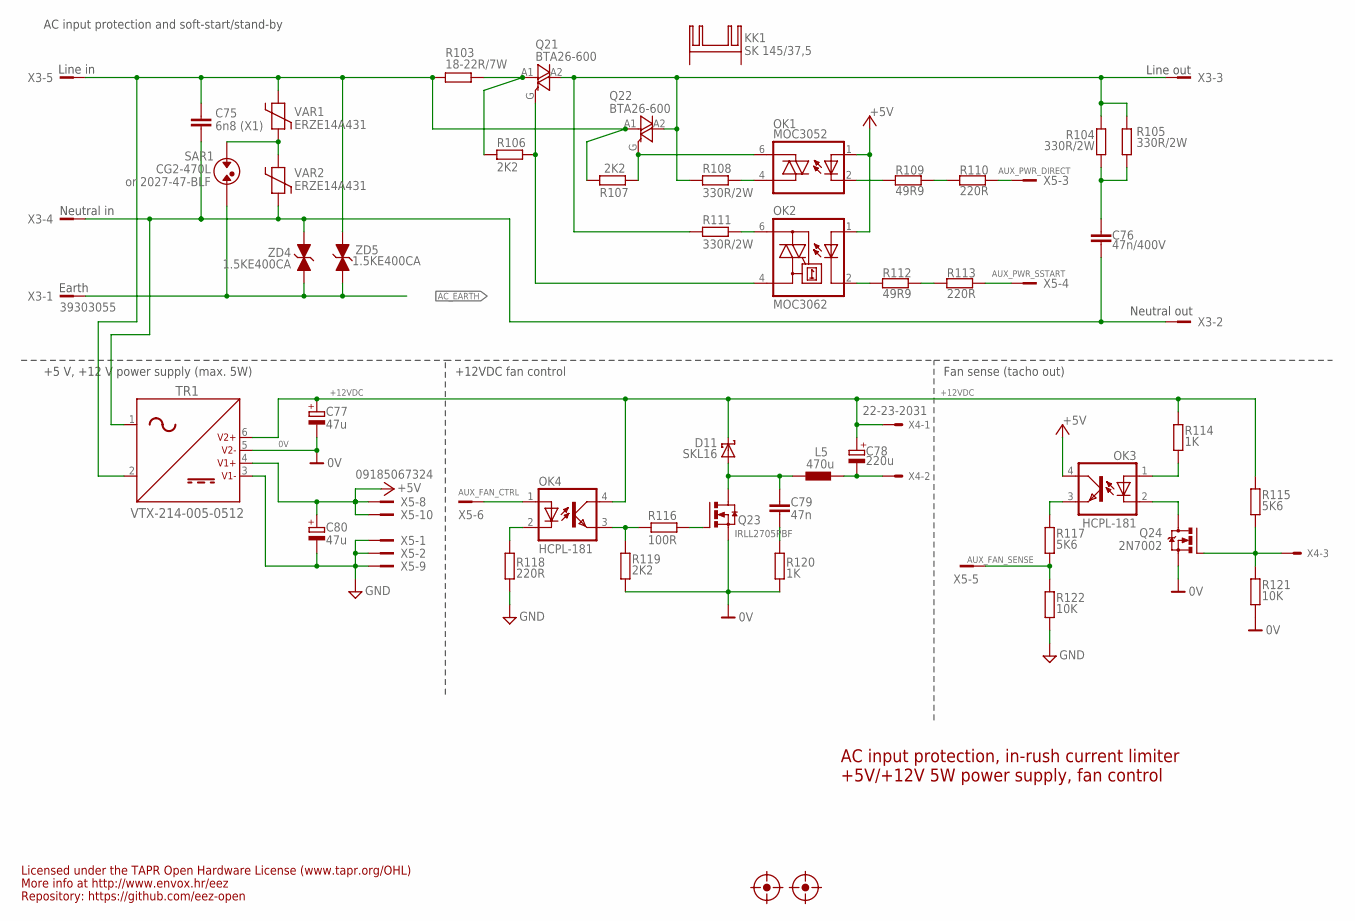
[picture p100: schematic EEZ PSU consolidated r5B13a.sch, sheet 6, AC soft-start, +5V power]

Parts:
C75: 6n8 (X1); C102-064X133
C76: 47n/400V; C075-052X106
C77, C80: 47u; CAPAE660X610N
C78: 220u; CAPAE660X610N
C79: 47n; C0805
D11: SKL16; SOD123
FM3, FM4: FIDUCIAL_2; FIDUCIAL_DUAL
KK1: SK 145/37,5; SK145
L5: 470u; DE0704
OK1: MOC3052; DIL6-SMD
OK2: MOC3062; DIL6-SMD; MPN MOC3033S-M
OK3, OK4: HCPL-181
Q21, Q22: BTA26-600; TOP3S-1
Q23: IRLL2705PBF; SOT223
Q24: 2N7002; SOT103P240X110-3N; MPN 2N7002-7-F
R103: 18-22R/7W; R_0913
R104, R105, R108, R111: 330R/2W; R2512
R106, R107, R119: 2K2; R0805
R109, R112: 49R9; R0805
R110, R113, R118: 220R; R0805
R114, R120: 1K; R0805
R115, R117: 5K6; R0805
R116: 100R; R0805
R121, R122: 10K; R0805
SAR1: CG2-470L; SAR
TR1: VTX-214-005-0512; PCB_ACDC_VTX_5W_DUAL
VAR1, VAR2: ERZE14A431; VARISTOR
X3: 39303055; MINIFIT_6659-5
X4: 22-23-2031
X5: 09185067324; IDC-10PIN
ZD4, ZD5: 1.5KE400CA; DO201-BIDIR

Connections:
0V: C77.2 (-), Q23.3 (S), Q24.2 (S), R119.1, R120.1, R121.2, TR1.5 (V2-)
+5V: C80.1 (+), OK1.1 (A), OK2.1 (A), OK3.4 (COL), TR1.4 (V1+), X5.8, X5.10; also elsewhere on the board
+12VDC: C77.1 (+), C78.1 (+), D11.C, OK4.4 (COL), R114.1, R115.1, TR1.6 (V2+), X4.1
AC_EARTH: SAR1.P$2, X3.1, ZD4.C (1), ZD5.C (1); also elsewhere on the board
AC_IN_L: C75.1, Q22.A1, R103.1, R107.2, TR1.2 (IN2), VAR1.P$2, X3.5, ZD5.A (2)
AC_NEUTRAL: C75.2, C76.1, TR1.1 (IN1), VAR2.P$1, X3.2, X3.4, ZD4.A (2)
AC_OUT_L: Q21.A2, Q22.A2, R104.1, R105.1, R108.2, R111.2, X3.3
AUX_FAN_CTRL: OK4.1 (A), X5.6
AUX_FAN_SENSE: R117.2, R122.1, X5.5
AUX_PWR_DIRECT: R110.2, X5.3
AUX_PWR_SSTART: R113.2, X5.4
FAN_OUT: C79.2, D11.A, L5.2, Q23.2 (D), Q23.4 (D)
GND: C80.2 (-), R118.2, R122.2, TR1.3 (V1-), X5.1, X5.2, X5.9; also elsewhere on the board
unnamed: OK3.3 (EMIT), R117.1
unnamed: Q24.1 (G), R115.2, R121.1, X4.3
unnamed: OK1.6 (A2), Q22.G, R107.1
unnamed: OK2.4 (A1), Q21.G, R106.2
unnamed: OK2.6 (A2), R111.1
unnamed: R109.2, R110.1
unnamed: R112.2, R113.1
unnamed: OK1.4 (A1), R108.1
unnamed: OK4.2 (C), R118.1
unnamed: C76.2, R104.2, R105.2
unnamed: C79.1, R120.2
unnamed: Q23.1 (G), R116.1
unnamed: C78.2 (-), L5.1, X4.2
unnamed: SAR1.P$1, VAR1.P$1, VAR2.P$2
unnamed: Q21.A1, R103.2, R106.1
unnamed: OK3.1 (A), R114.2
unnamed: OK4.3 (EMIT), R116.2, R119.2
unnamed: OK2.2 (C), R112.1
unnamed: OK1.2 (C), R109.1
unnamed: OK3.2 (C), Q24.3 (D)

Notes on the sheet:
AC input protection, in-rush current limiter
+5V/+12V 5W power supply, fan control
Line in
Neutral in
Earth
Line out
Neutral out
or 2027-47-BLF
Licensed under the TAPR Open Hardware License (www.tapr.org/OHL)
Repository: https://github.com/eez-open
More info at http://www.envox.hr/eez
+5 V, +12 V power supply (max. 5W)
AC input protection and soft-start/stand-by
+12VDC fan control
Fan sense (tacho out)

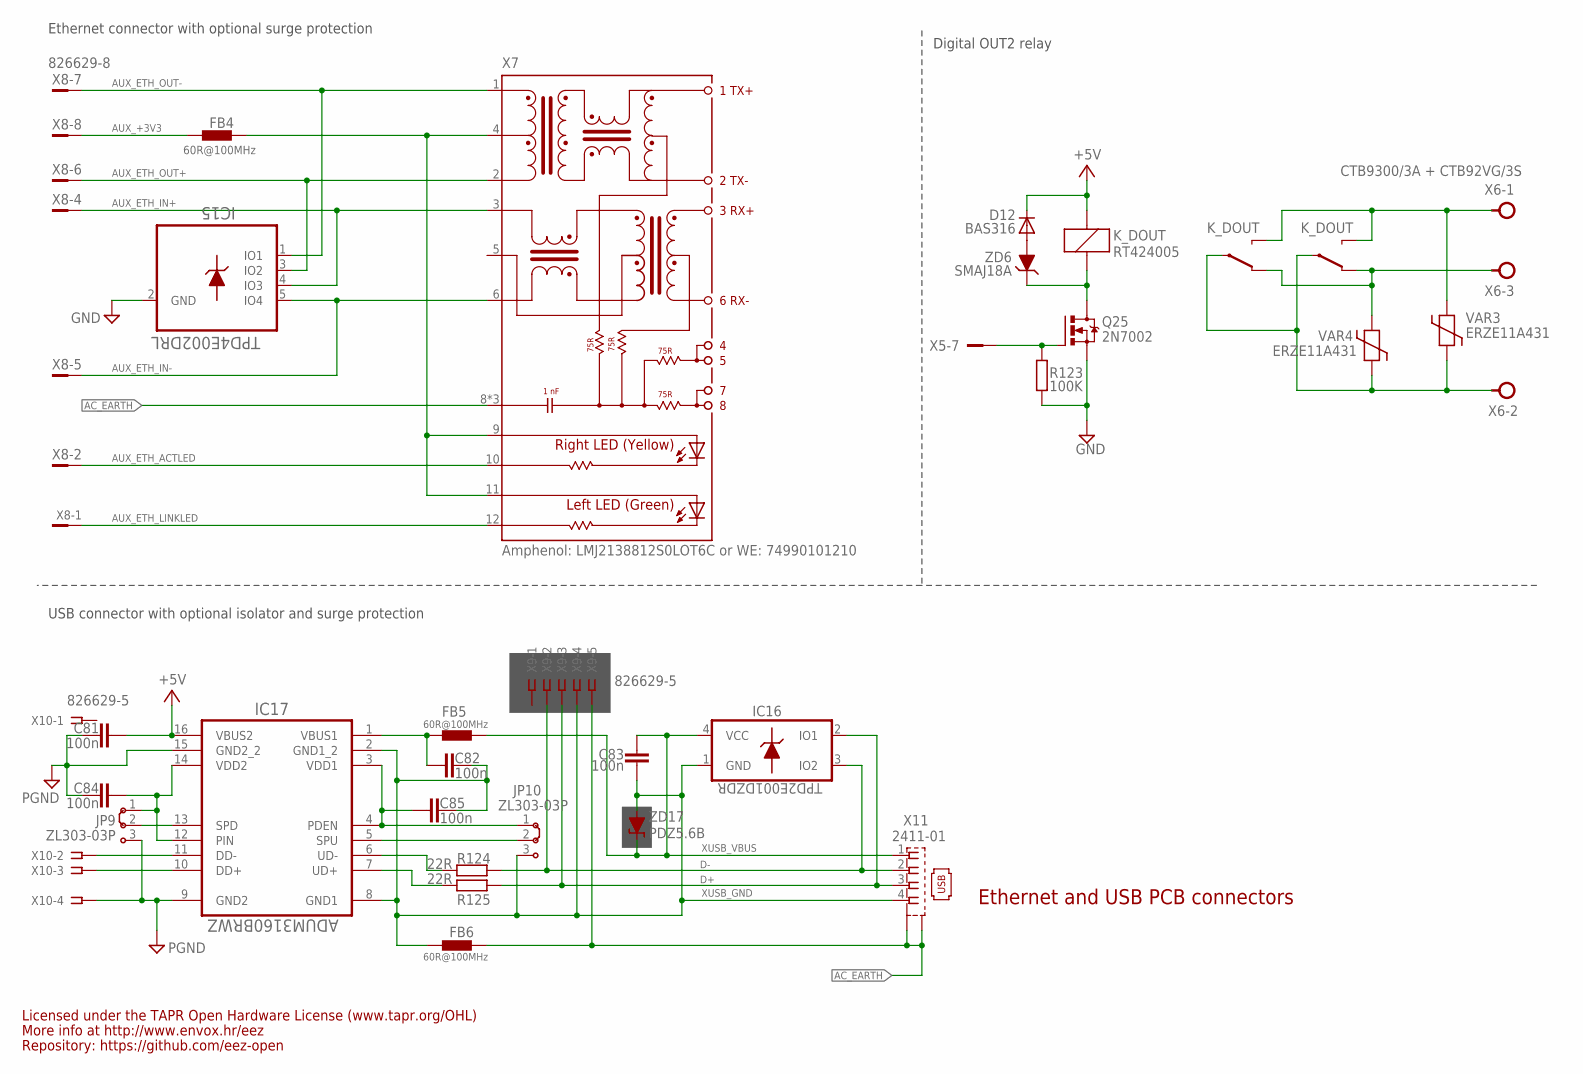
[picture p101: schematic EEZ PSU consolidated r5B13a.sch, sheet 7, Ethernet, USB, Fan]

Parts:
C81, C82, C83, C84, C85: 100n; C0603
D12: BAS316; SOD323-W
FB4, FB5, FB6: 60R@100MHz; BEAD0603
IC15: TPD4E002DRL; DRL5
IC16: TPD2E001DZDR; SOP192P292X122-4N
IC17: ADUM3160BRWZ; SOIC-16W
JP9, JP10: ZL303-03P
K_DOUT: RT424005; RT-C/016A5_ROUND
Q25: 2N7002; SOT103P240X110-3N
R123: 100K; R0805
R124, R125: 22R; R0805
VAR3, VAR4: ERZE11A431; VARISTOR_13MM
X5: 09185067324; IDC-10PIN
X6: CTB9300/3A + CTB92VG/3S; WR-TBL_3-PIN
X7: Amphenol: LMJ2138812S0LOT6C or WE: 74990101210; RJ45-VERT
X8: 826629-8; HEADER_8-PIN
X9, X10: 826629-5; SSW-105-02-S-S
X11: 2411-01; KUSBVX-BS1N
ZD6: SMAJ18A; DO214AC
ZD17: PDZ5.6B; SOD323-W

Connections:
+5V: C81.1, D12.C, IC17.16 (VBUS2), K_DOUT.A1 (C2); also elsewhere on the board
AC_EARTH: FB6.P$1 (1), X7.8 (SH), X7.SH1 (SH), X7.SH2 (SH), X9.5, X11.M1 (S1), X11.M2 (S2); also elsewhere on the board
AUX_+3V3: FB4.P$2 (2), X8.8
AUX_ETH_ACTLED: X7.10 (YELLOW-C), X8.2
AUX_ETH_IN+: IC15.4 (IO3), X7.3 (RD+), X8.4
AUX_ETH_IN-: IC15.5 (IO4), X7.6 (RD-), X8.5
AUX_ETH_LINKLED: X7.12 (GREEN-C), X8.1
AUX_ETH_OUT+: IC15.3 (IO2), X7.2 (TD-), X8.6
AUX_ETH_OUT-: IC15.1 (IO1), X7.1 (TD+), X8.7
D+: IC16.2 (IO1), R125.1, X9.3, X11.3
D-: IC16.3 (IO2), R124.1, X9.2, X11.2
GND: C81.2, C84.2, IC15.2 (GND), IC17.9 (GND2), IC17.15 (GND2_2), JP9.3, Q25.2 (S), R123.1, X10.4; also elsewhere on the board
MCU_D+: IC17.10 (DD+), X10.3
MCU_D-: IC17.11 (DD-), X10.2
unnamed: FB4.P$1 (1), X7.4 (CT), X7.9 (YELLOW_A), X7.11 (GREEN-A)
unnamed: IC17.13 (SPD), JP9.2
unnamed: K_DOUT.14A (O), K_DOUT.14B (O), VAR3.2, X6.1
unnamed: K_DOUT.11A, K_DOUT.11B, VAR3.1, VAR4.1, X6.2
unnamed: Q25.1 (G), R123.2, X5.7
unnamed: D12.A, ZD6.A
unnamed: K_DOUT.A2 (C1), Q25.3 (D), ZD6.C
unnamed: C85.1, IC17.3 (VDD1), IC17.4 (PDEN), JP10.1
unnamed: IC17.6 (UD-), R124.2
unnamed: IC17.7 (UD+), R125.2
unnamed: C82.1, FB5.P$2 (2), IC17.1 (VBUS1)
unnamed: C84.1, IC17.12 (PIN), IC17.14 (VDD2), JP9.1
unnamed: IC17.5 (SPU), JP10.2
unnamed: K_DOUT.12A (S), K_DOUT.12B (S), VAR4.2, X6.3
XUSB_GND: C82.2, C83.1, C85.2, FB6.P$2 (2), IC16.1 (GND), IC17.2 (GND1_2), IC17.8 (GND1), JP10.3, X9.4, X11.4, ZD17.A
XUSB_VBUS: C83.2, FB5.P$1 (1), IC16.4 (VCC), X11.1, ZD17.C

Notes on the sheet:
Ethernet and USB PCB connectors
Licensed under the TAPR Open Hardware License (www.tapr.org/OHL)
Repository: https://github.com/eez-open
More info at http://www.envox.hr/eez
Ethernet connector with optional surge protection
USB connector with optional isolator and surge protection
Digital OUT2 relay

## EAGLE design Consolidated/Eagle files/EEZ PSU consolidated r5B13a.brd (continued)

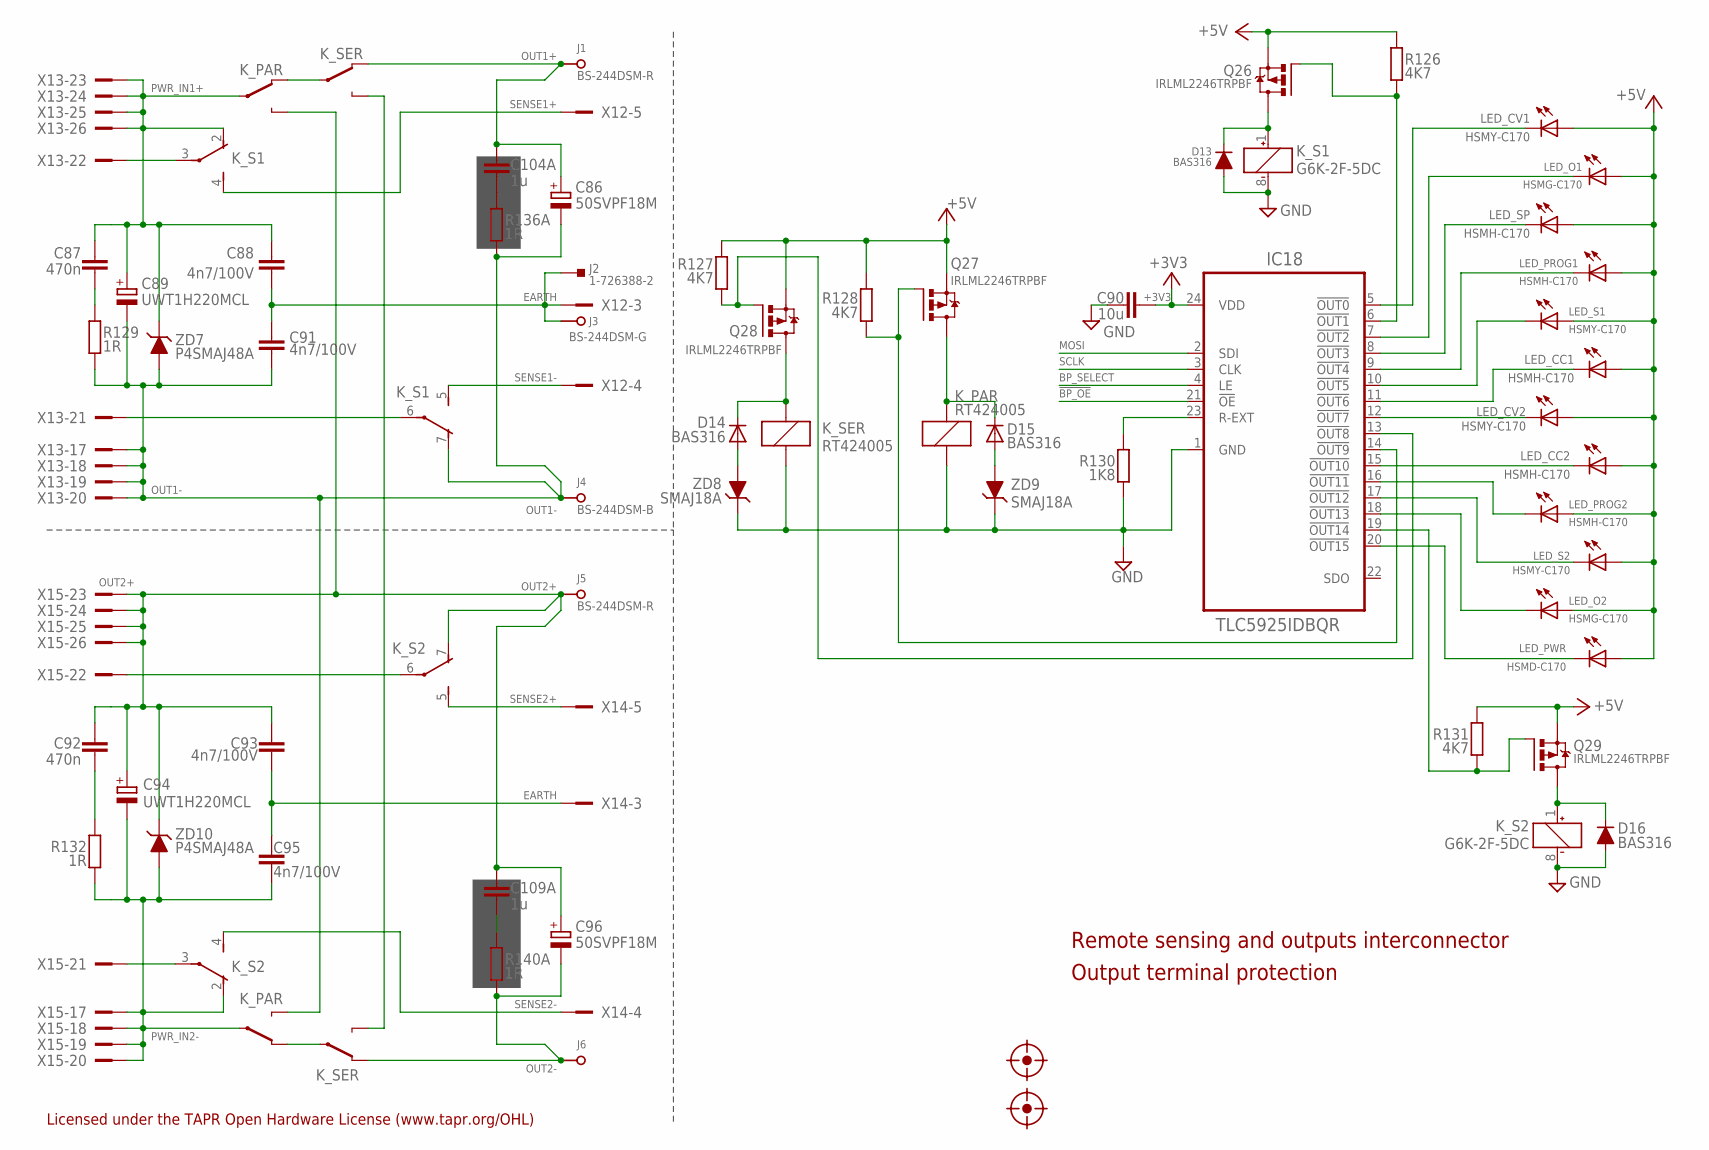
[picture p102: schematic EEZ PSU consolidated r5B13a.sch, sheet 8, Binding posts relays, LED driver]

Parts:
C86, C96: 50SVPF18M; CAPAE830X650N; TOLERANCE ±20 %; VOLTAGERATING 63V; MPN EEE-FK1J220P
C87, C92: 470n; C0805
C88, C91, C93, C95: 4n7/100V; C1210
C89, C94: UWT1H220MCL; CAPAE830X650N
C90: 10u; C1210
C104A, C109A: 1u; C0805
D13, D16: BAS316; SOD323-R
D14, D15: BAS316; SOD323-W
FM5, FM6: FIDUCIAL_2; FIDUCIAL_DUAL
IC18: TLC5925IDBQR; SOP63P600X175-24N
J1, J5: BS-244DSM-R; BP_5_12
J2: 1-726388-2; PCB_TAB-4.8MM
J3: BS-244DSM-G; BP_5_12
J4, J6: BS-244DSM-B; BP_5_12
K_PAR: RT424005; RT-C/016A5_ROUND
K_S1, K_S2: G6K-2F-5DC; G6K-2F; MPN G6K-2F DC24
K_SER: RT424005; RT-C/016A5_ROUND
LED_CC1, LED_CC2: HSMH-C170; LED_HSMH-C170
LED_CV1, LED_CV2: HSMY-C170; LED_0805
LED_O1, LED_O2: HSMG-C170; LED_0805
LED_PROG1, LED_PROG2: HSMH-C170; LED_HSMH-C170
LED_PWR: HSMD-C170; LED_0805
LED_S1, LED_S2: HSMY-C170; LED_0805
LED_SP: HSMH-C170; LED_HSMH-C170
Q26, Q27, Q28, Q29: IRLML2246TRPBF; SOT95P237X112-3N
R126, R127, R128, R131: 4K7; R0805
R129, R132, R136A, R140A: 1R; R0805
R130: 1K8; R0805
X12: MC000006; MC000006_MIRROR; FARNELL 2007972
X13, X15: TSW-113-07-F-D; FARNELL 2025182
X14: MC000006; MC000006_MIRROR
ZD7, ZD10: P4SMAJ48A; DO214AC
ZD8, ZD9: SMAJ18A; DO214AC

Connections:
!BP_OE: IC18.21 (!OE); also elsewhere on the board
!BP_OUT0: IC18.5 (!OUT0), LED_CV1.C
!BP_OUT1: IC18.6 (!OUT1), Q26.1 (G), R126.1
!BP_OUT2: IC18.7 (!OUT2), LED_O1.C
!BP_OUT3: IC18.8 (!OUT3), LED_SP.C
!BP_OUT4: IC18.9 (!OUT4), LED_PROG1.C
!BP_OUT5: IC18.10 (!OUT5), LED_S1.C
!BP_OUT6: IC18.11 (!OUT6), LED_CC1.C
!BP_OUT7: IC18.12 (!OUT7), LED_CV2.C
!BP_OUT8: IC18.13 (!OUT8), Q28.1 (G), R127.1
!BP_OUT9: IC18.14 (!OUT9), Q27.1 (G), R128.1
!BP_OUT10: IC18.15 (!OUT10), LED_CC2.C
!BP_OUT12: IC18.17 (!OUT12), LED_S2.C
!BP_OUT13: IC18.18 (!OUT13), LED_O2.C
!BP_OUT14: IC18.19 (!OUT14), Q29.1 (G), R131.1
!BP_OUT15: IC18.20 (!OUT15), LED_PWR.C
+3V3: C90.1, IC18.24 (VDD); also elsewhere on the board
+5V: LED_CC1.A, LED_CC2.A, LED_CV1.A, LED_CV2.A, LED_O1.A, LED_O2.A, LED_PROG1.A, LED_PROG2.A, LED_PWR.A, LED_S1.A, LED_S2.A, LED_SP.A, Q26.2 (S), Q27.2 (S), Q28.2 (S), Q29.2 (S), R126.2, R127.2, R128.2, R131.2; also elsewhere on the board
BP_SELECT: IC18.4 (LE); also elsewhere on the board
EARTH: C88.2, C91.1, C93.2, C95.1, J2.P$1, J2.P$2, J3.P$1, X12.3, X12.3.1, X14.3, X14.3.1; also elsewhere on the board
GND: C90.2, D13.A, D16.A, IC18.1 (GND), K_PAR.A1 (C2), K_S1.8 (-), K_S2.8 (-), K_SER.A1 (C2), R130.1, ZD8.C, ZD9.C; also elsewhere on the board
MOSI: IC18.2 (SDI); also elsewhere on the board
unnamed: D13.C, K_S1.1 (+), Q26.3 (D)
unnamed: D16.C, K_S2.1 (+), Q29.3 (D)
unnamed: C87.2, R129.2
unnamed: C92.2, R132.2
unnamed: IC18.16 (!OUT11), LED_PROG2.C
unnamed: K_SER.14A (O), K_SER.14B (O)
unnamed: K_PAR.12A (S), K_SER.11B
unnamed: K_PAR.12B (S), K_SER.11A
unnamed: D14.A, ZD8.A
unnamed: D15.A, ZD9.A
unnamed: D14.C, K_SER.A2 (C1), Q28.3 (D)
unnamed: D15.C, K_PAR.A2 (C1), Q27.3 (D)
unnamed: C104A.2, R136A.2
unnamed: C109A.2, R140A.2
unnamed: IC18.23 (R-EXT), R130.2
OUT1+: C86.1, C104A.1, J1.P$1, K_SER.12B (S)
OUT1-: C86.2, C89.2, C91.2, J4.P$1, K_PAR.14B (O), K_S1.7 (O), R129.1, R136A.1, X13.17, X13.18, X13.19, X13.20, ZD7.A
OUT2+: C92.1, C93.1, C94.1, C96.1, C109A.1, J5.P$1, K_PAR.14A (O), K_S2.7 (O), X15.23, X15.24, X15.25, X15.26, ZD10.C
OUT2-: C96.2, J6.P$1, K_SER.12A (S), R140A.1
PWR_IN1+: C87.1, C88.1, C89.1, K_PAR.11A, K_S1.2 (O), X13.23, X13.24, X13.25, X13.26, ZD7.C
PWR_IN2-: C94.2, C95.2, K_PAR.11B, K_S2.2 (O), R132.1, X15.17, X15.18, X15.19, X15.20, ZD10.A
SCLK: IC18.3 (CLK); also elsewhere on the board
SENSE1+: K_S1.4 (S), X12.5, X12.5.1
SENSE1-: K_S1.5 (S), X12.4, X12.4.1
SENSE1_IN+: K_S1.3, X13.22
SENSE1_IN-: K_S1.6, X13.21
SENSE2+: K_S2.5 (S), X14.5, X14.5.1
SENSE2-: K_S2.4 (S), X14.4, X14.4.1
SENSE2_IN+: K_S2.6, X15.22
SENSE2_IN-: K_S2.3, X15.21

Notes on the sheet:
Remote sensing and outputs interconnector
Output terminal protection
Licensed under the TAPR Open Hardware License (www.tapr.org/OHL)

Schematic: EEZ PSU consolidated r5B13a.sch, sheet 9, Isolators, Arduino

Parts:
C97, C98, C99, C100, C101, C102, C104, C106, C107: 100n; C0603
C103: 47u; CAPAE660X610N
C105: 10u; EC1206
D17: SMBJ5.0A-TR; DO214AA
IC19, IC23: Si8641EC-B-IS1; SOIC-16
IC20, IC21: SI8651EC-B-IS1; SOIC-16
IC22: LD1117ADT33TR; SOT223
MCU: Arduino Due; ARDUINO+ICSP_MIRROR
SW1: A101SYCQ04; M9040P
X13, X15: TSW-113-07-F-D; FARNELL 2025182
X16: 09185067324; IDC-10PIN

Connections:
!ADC1_SELECT: IC20.4 (A3), MCU.15
!ADC2_SELECT: IC23.4 (A2), MCU.48 (48(PL3))
!BP_OE: MCU.10; also elsewhere on the board
!CH1_ADC: IC20.13 (B3), X13.6
!CH1_DAC: IC19.12 (B3), X13.4
!CH1_EXPANDER: IC19.13 (B2), X13.3
!CH1_INT: IC20.11 (B5), X13.8
!CH1_RESET: IC20.14 (B2), X13.5
!CH2_ADC: IC23.13 (B2), X15.6
!CH2_DAC: IC21.12 (B4), X15.4
!CH2_EXPANDER: IC21.13 (B3), X15.3
!CH2_INT: IC21.11 (B5), X15.8
!CH2_RESET: IC23.14 (B1), X15.5
!CONVEND1: IC20.6 (A5), MCU.21
!CONVEND2: IC21.6 (A5), MCU.20
!DAC1_SELECT: IC19.5 (A3), MCU.16
!DAC2_SELECT: IC21.5 (A4), MCU.47 (47(PL4))
!EEPROM_SELECT: MCU.49 (49(PL2)); also elsewhere on the board
!ETH_IRQ: MCU.18; also elsewhere on the board
!ETH_SELECT: MCU.11; also elsewhere on the board
!IO_EXPANDER1: IC19.4 (A2), MCU.17
!IO_EXPANDER2: IC21.4 (A3), MCU.46 (46(PL5))
!LCD_INT: MCU.50 (50(PL1/MISO)); also elsewhere on the board
!LCD_PD: MCU.51 (51(PL0)); also elsewhere on the board
!RESET: IC20.3 (A2), IC23.3 (A1), MCU.RESET (!RESET); also elsewhere on the board
!RTC_IRQ: MCU.19; also elsewhere on the board
+3V3: C98.1, C99.1, C101.1, C105.+, C107.1, IC19.1 (VDD1), IC20.1 (VDD1), IC20.7 (EN1), IC21.1 (VDD1), IC21.7 (EN1), IC22.4 (OUT), IC23.1 (VDD1); also elsewhere on the board
+5V: C103.1 (+), C104.1, D17.C, IC22.3 (IN), MCU.5V, SW1.3 (S); also elsewhere on the board
BATT_NTC: MCU.A4 (ADC4); also elsewhere on the board
BP_SELECT: MCU.9 (9(PH6)); also elsewhere on the board
BUZZER: MCU.12; also elsewhere on the board
CH1_GND: C97.2, C100.2, IC19.9 (GND2_2), IC19.15 (GND2), IC20.9 (GND2), X13.10, X13.12, X13.14; also elsewhere on the board
CH1_MISO: IC19.11 (B4), X13.9
CH1_MOSI: IC19.14 (B1), X13.1
CH1_SCLK: IC20.12 (B4), X13.7
CH1_SYNC: IC20.15 (B1), X13.16
CH1_VDD: C97.1, C100.1, IC19.10 (EN2), IC19.16 (VDD2), IC20.10 (EN2), IC20.16 (VDD2), X13.2; also elsewhere on the board
CH2_GND: C102.2, C106.2, IC21.9 (GND2), IC23.9 (GND2_2), IC23.15 (GND2), X15.10, X15.12, X15.14; also elsewhere on the board
CH2_MISO: IC23.11 (B4), X15.9
CH2_MOSI: IC21.14 (B2), X15.1
CH2_SCLK: IC23.12 (B3), X15.7
CH2_SYNC: IC21.15 (B1), X15.16
CH2_VDD: C102.1, C106.1, IC21.10 (EN2), IC21.16 (VDD2), IC23.10 (EN2), IC23.16 (VDD2), X15.2
DOUT1: MCU.A11 (ADC11); also elsewhere on the board
DOUT2: MCU.A3 (ADC3); also elsewhere on the board
ENC_A: MCU.A9 (ADC9); also elsewhere on the board
ENC_B: MCU.A8 (ADC8); also elsewhere on the board
ENC_SW: MCU.A10 (ADC10); also elsewhere on the board
EXTSD_CS: MCU.A12 (ADC12); also elsewhere on the board
EXT_TRIG: MCU.A7 (ADC7); also elsewhere on the board
FAN_PWM: MCU.6 (6(PH3)), X16.6
FAN_SENSE: MCU.13, X16.5
GND: C98.2, C99.2, C101.2, C103.2 (-), C104.2, C105.-, C107.2, D17.A, IC19.2 (GND1_2), IC19.8 (GND1), IC20.8 (GND1), IC21.8 (GND1), IC22.1 (ADJ), IC23.2 (GND1_2), IC23.8 (GND1), MCU.GND, MCU.GND1, MCU.GND2, MCU.GND3, MCU.GND4, MCU.ICSP_GND (GND), X16.1, X16.2, X16.9; also elsewhere on the board
ISOLATOR1_EN: IC19.7 (EN1), MCU.14
ISOLATOR2_EN: IC23.7 (EN1), MCU.45 (45(PL6))
LCDSD_CS: MCU.53 (53(PB2/MOSI)); also elsewhere on the board
LCD_BRIGHTNESS: MCU.7 (7(PH4)); also elsewhere on the board
LCD_CS: MCU.39 (39(PC0)); also elsewhere on the board
LCD_DB0: MCU.37 (37(PC2)); also elsewhere on the board
LCD_DB1: MCU.36 (36(PC3)); also elsewhere on the board
LCD_DB2: MCU.35 (35(PC4)); also elsewhere on the board
LCD_DB3: MCU.34 (34(PC5)); also elsewhere on the board
LCD_DB4: MCU.33 (33(PC6)); also elsewhere on the board
LCD_DB5: MCU.32 (32(PC7)); also elsewhere on the board
LCD_DB6: MCU.31 (31(PA7)); also elsewhere on the board
LCD_DB7: MCU.30 (30(PA6)); also elsewhere on the board
LCD_DB8: MCU.22; also elsewhere on the board
LCD_DB9: MCU.23; also elsewhere on the board
LCD_DB10: MCU.24 (24(PA0)); also elsewhere on the board
LCD_DB11: MCU.25 (25(PA1)); also elsewhere on the board
LCD_DB12: MCU.26 (26(PA2)); also elsewhere on the board
LCD_DB13: MCU.27 (27(PA3)); also elsewhere on the board
LCD_DB14: MCU.28 (28(PA4)); also elsewhere on the board
LCD_DB15: MCU.29 (29(PA5)); also elsewhere on the board
LCD_RESET: MCU.38 (38(PC1)); also elsewhere on the board
LCD_RS: MCU.41 (41(PG2)); also elsewhere on the board
LCD_WR: MCU.40 (40(PD7)); also elsewhere on the board
MISO: IC19.6 (A4), IC23.6 (A4), MCU.ICSP_MISO (MISO); also elsewhere on the board
MOSI: IC19.3 (A1), IC21.3 (A2), MCU.ICSP_MOSI (MOSI); also elsewhere on the board
unnamed: SW1.2, X16.8, X16.10
NTC1: MCU.A5 (ADC5); also elsewhere on the board
NTC2: MCU.A6 (ADC6); also elsewhere on the board
PWRDIR: MCU.A1 (ADC1); also elsewhere on the board
PWRSS: MCU.A2 (ADC2); also elsewhere on the board
PWR_DIRECT: X16.3; also elsewhere on the board
PWR_SSTART: X16.4; also elsewhere on the board
RTC_SELECT: MCU.8 (8(PH5)); also elsewhere on the board
SCLK: IC20.5 (A4), IC23.5 (A3), MCU.ICSP_SCK (SCK); also elsewhere on the board
SYNC1: IC20.2 (A1); also elsewhere on the board
SYNC2: IC21.2 (A1); also elsewhere on the board
SYNC_MASTER: MCU.4 (4(PG5)); also elsewhere on the board
TEMP_ANALOG: MCU.A0 (ADC0); also elsewhere on the board
TOUCH_CS: MCU.43 (43(PG0)); also elsewhere on the board
TOUCH_DIN: MCU.42 (42(PG1)); also elsewhere on the board
TOUCH_DOUT: MCU.3 (3(PE5)); also elsewhere on the board
TOUCH_IRQ: MCU.2 (2(PE4)); also elsewhere on the board
TOUCH_SCLK: MCU.44 (44(PL7)); also elsewhere on the board
WATCHDOG: MCU.5 (5(PE3)); also elsewhere on the board

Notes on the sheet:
I/O isolators for communication with
post-regulator PCB, Arduino breakout
Ch #1 bus isolators
Ch #2 bus isolators
Arduino board breakout
Licensed under the TAPR Open Hardware License (www.tapr.org/OHL)

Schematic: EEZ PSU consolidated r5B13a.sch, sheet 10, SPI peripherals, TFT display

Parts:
C108, C109, C111, C113, C114, C121, C122, C123, C124, C125, C126, C127, C128: 100n; C0603
C110: 10u; C1210
C112: EECS5R5H105; SG-R20MM
C115: 22n; C0805
C116, C120: 18p; C0805
C117, C119: 6n8; C0603
C118, C131: 10n; C0805
C129: 10u; EC1206
C130: 4u7; EC1206
D18: BAS316; SOD323-W
IC24: PCA21125T/Q900/1,1; SOP65P640X120-14N
IC25: AT25256B-SSHL-B; SOIC127P600X175-8N
IC26: W5500; TQFP48-7X7
JP4: JP3-CUT
LCD1: TFT_320QVT; LCD_TFT_9341_MIRROR
Q30: 2N7002; SOT103P240X110-3N
Q31: IRLML2246TRPBF; SOT95P237X112-3N
R133, R136, R137: 4K7; R0805
R134, R147, R148: 180R; R0805
R135, R146: 100K; R0805
R138, R140, R141, R142: 49R9; R0805
R139, R145, R149: 10K; R0805
R143: 10R; R1206
R144: 12K4; R0805
R176: 1M; R0805
RN1, RN2: 4x10K; CAY16
SH3: SHORTNOHOLE; SHORT_NOHOLE
SP1: LD-BZEN-0903
X13, X15: TSW-113-07-F-D; FARNELL 2025182
X17: 22-23-2021; MPN 22-23-2021
X18: MC34753; HEADER_8-PIN
Y1: 32.768kHz; R26_XTAL
Y2: 25MHz; HC-49/4H

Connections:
1V2O: C131.2, IC26.22 (1V2O)
!EEPROM_SELECT: IC25.1 (!CS); also elsewhere on the board
!ETH_IRQ: IC26.36 (INTN); also elsewhere on the board
!ETH_SELECT: IC26.32 (SCSN); also elsewhere on the board
!RESET: IC26.37 (RSTN); also elsewhere on the board
!RTC_IRQ: IC24.5 (!INT); also elsewhere on the board
+3V3: C110.2, C111.1, C115.1, C121.2, C123.1, C124.1, C125.1, C126.1, C127.1, C128.1, C129.+, D18.A, IC25.3 (!WP), IC25.7 (!HOLD), IC25.8 (VCC), IC26.4 (AVDD), IC26.8 (AVDD1), IC26.11 (AVDD2), IC26.15 (AVDD3), IC26.17 (AVDD4), IC26.21 (AVDD5), IC26.28 (VDD), JP4.NO, Q31.2 (S), R138.1, R139.2, R140.2, R146.2, RN2.6 (2), RN2.7 (2), RN2.8 (2), SP1.+B (+), X17.1, X18.8; also elsewhere on the board
+5V: JP4.NC; also elsewhere on the board
BUZZER: Q30.1 (G), R135.2; also elsewhere on the board
EARTH: C115.2, C118.2, X18.3; also elsewhere on the board
ETH_ACTLED: IC26.27 (ACTLED), R147.1
ETH_IN+: C119.1, R142.1, X18.4
ETH_IN-: C117.1, R141.2, X18.5
ETH_LINKLED: IC26.25 (LINKLED), R148.1
ETH_OUT+: IC26.2 (TXP), R140.1, X18.6
ETH_OUT-: IC26.1 (TXN), R138.2, X18.7
GND: C108.1, C109.1, C110.1, C111.2, C112.2 (-), C113.1, C114.1, C116.2, C120.2, C121.1, C122.1, C123.2, C124.2, C125.2, C126.2, C127.2, C128.2, C129.-, C131.1, IC24.7 (VSS), IC25.4 (GND), IC26.29 (GND), LCD1.1 (GND), Q30.2 (S), R133.2, R135.1, R136.2, R137.2, R149.1, RN1.5 (2), RN1.6 (2), RN1.7 (2), RN1.8 (2), RN2.5 (2), SH3.P$1 (GND_A); also elsewhere on the board
GNDA: C130.-, IC26.3 (AGND), IC26.9 (AGND1), IC26.14 (AGND2), IC26.16 (AGND3), IC26.19 (AGND4), IC26.48 (AGND5), R144.1, SH3.P$2 (GND_B)
LCDSD_CS: LCD1.38 (SD_CS); also elsewhere on the board
LCD_BRIGHTNESS: R145.1; also elsewhere on the board
LCD_CS: LCD1.15 (CS); also elsewhere on the board
LCD_DB0: LCD1.21 (DB0); also elsewhere on the board
LCD_DB1: LCD1.22 (DB1); also elsewhere on the board
LCD_DB2: LCD1.23 (DB2); also elsewhere on the board
LCD_DB3: LCD1.24 (DB3); also elsewhere on the board
LCD_DB4: LCD1.25 (DB4); also elsewhere on the board
LCD_DB5: LCD1.26 (DB5); also elsewhere on the board
LCD_DB6: LCD1.27 (DB6); also elsewhere on the board
LCD_DB7: LCD1.28 (DB7); also elsewhere on the board
LCD_DB8: LCD1.7 (DB8); also elsewhere on the board
LCD_DB9: LCD1.8 (DB9); also elsewhere on the board
LCD_DB10: LCD1.9 (DB10); also elsewhere on the board
LCD_DB11: LCD1.10 (DB11); also elsewhere on the board
LCD_DB12: LCD1.11 (DB12); also elsewhere on the board
LCD_DB13: LCD1.12 (DB13); also elsewhere on the board
LCD_DB14: LCD1.13 (DB14); also elsewhere on the board
LCD_DB15: LCD1.14 (DB15); also elsewhere on the board
LCD_RD: LCD1.6 (RD), R139.1
LCD_RESET: LCD1.17 (RST); also elsewhere on the board
LCD_RS: LCD1.4 (RS); also elsewhere on the board
LCD_WR: LCD1.5 (WR); also elsewhere on the board
LED_A: LCD1.19 (LED_A), R143.2
MISO: IC24.8 (SDO), IC25.2 (SO), IC26.34 (MISO), LCD1.35 (SD_DO); also elsewhere on the board
MOSI: IC24.9 (SDI), IC25.5 (SI), IC26.35 (MOSI), LCD1.37 (SD_IN); also elsewhere on the board
unnamed: Q30.3 (D), SP1.-B (-)
unnamed: JP4.COM, LCD1.2 (VCC)
unnamed: Q31.3 (D), R143.1
unnamed: C112.1 (+), R134.1
unnamed: IC26.23 (RSVD), R149.2
unnamed: C108.2, D18.C, IC24.14 (VDD), R134.2
unnamed: IC26.10 (EXRES1), R144.2
unnamed: C116.1, IC26.31 (XO), R176.2, Y2.1
unnamed: C120.1, IC26.30 (XI/CLKIN), R176.1, Y2.2
unnamed: C117.2, IC26.5 (RXN)
unnamed: C119.2, IC26.6 (RXP)
unnamed: R148.2, X18.1
unnamed: R147.2, X18.2
unnamed: IC26.43 (PMODE2), RN2.3 (1)
unnamed: IC26.44 (PMODE1), RN2.2 (1)
unnamed: IC26.45 (PMODE0), RN2.1
unnamed: IC26.42 (RSVD5), RN2.4 (1)
unnamed: IC26.38 (RSVD1), RN1.4 (1)
unnamed: C118.1, R141.1, R142.2
unnamed: IC26.39 (RSVD2), RN1.3 (1)
unnamed: IC26.41 (RSVD4), RN1.1
unnamed: IC26.40 (RSVD3), RN1.2 (1)
unnamed: C122.2, Q31.1 (G), R145.2, R146.1
unnamed: IC24.1 (OSCI), Y1.2
unnamed: IC24.2 (OSCO), Y1.1
NTC1: C109.2, R133.1, X13.13; also elsewhere on the board
NTC2: C114.2, R137.1, X15.13; also elsewhere on the board
RTC_SELECT: IC24.6 (CE); also elsewhere on the board
SCLK: IC24.10 (SCL), IC25.6 (SCK), IC26.33 (SCLK), LCD1.36 (SD_CLK); also elsewhere on the board
TEMP_ANALOG: C113.2, R136.1, X17.2; also elsewhere on the board
TOCAP: C130.+, IC26.20 (TOCAP)
TOUCH_CS: LCD1.30 (T_CS); also elsewhere on the board
TOUCH_DIN: LCD1.31 (T_DIN); also elsewhere on the board
TOUCH_DOUT: LCD1.33 (T_DO); also elsewhere on the board
TOUCH_IRQ: LCD1.34 (T_IRQ); also elsewhere on the board
TOUCH_SCLK: LCD1.29 (T_CLK); also elsewhere on the board

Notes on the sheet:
TFT-touchscreen, RTC, EEPROM, Ethernet
e.g. Farnell: 1187100
10K NTC
or TME: NTC-K45-10
Buzzer, temperature sensor (NTC)
External EEPROM
Real time clock
Buzzer
Temperature sensors
TFT touch scrreen with SD-card
Ethernet
controller
Licensed under the TAPR Open Hardware License (www.tapr.org/OHL)
Repository: https://github.com/eez-open
More info at http://www.envox.hr/eez

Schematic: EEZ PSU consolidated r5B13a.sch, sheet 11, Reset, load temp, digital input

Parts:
C132, C134, C136, C139, C141: 100n; C0603
C133, C140: 47n; C0805
C135, C137, C138: 10n; C0805
C156: 1u; C0805
D19: BAT54S; SOT23
D20: SKL16; SOD123
D21: BAS316; SOD323-R
F1: 50mA; F1210
FB7: 60R@100MHz; BEAD0603
IC27: BC857BS; SOT65P210X110-6N
IC28: TLC555; SOIC127P600X175-8N
IC29: SN74LVC08APWR; SOP65P640X120-14N
IC30: SN74LV1T34DBVR; SOT95P280X145-5N
IC31: TPS3705-33D; SOIC127P600X175-8N
IC32: SN74LVC2G02DCTR; SOP65P400X130-8N
OK5, OK6: HCPL-181
Q32, Q33: 2N7002; SOT103P240X110-3N
R150: 180R; R0805
R151: 1K8; R0805
R152, R153: 750R; R0805
R154, R158: 47K; R0805
R155: 100R; R0805
R156, R159, R161, R162: 4K7; R0805
R157, R165: 10K; R0805
R160, R178: 100K; R0805
R163, R164: 1K; R0805
R166, R177: 220R; R0805
SW2: PEC12R-4225F-S0024; EC12E_SW
SW3: 1301.9316; TACTM-6XN
X12: MC000006; MC000006_MIRROR; FARNELL 2007972
X13, X15: TSW-113-07-F-D; FARNELL 2025182
X14: MC000006; MC000006_MIRROR
X16: 09185067324; IDC-10PIN
ZD11, ZD12, ZD14: SMAJ18A; DO214AC
ZD13: 4V3; MINIMELF

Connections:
!MR: C140.2, IC31.1 (!MR), IC31.8 (!WDO), SW3.3, SW3.4
!RESET: D21.A, IC29.1 (I0), R160.1; also elsewhere on the board
!RST_OUT: IC29.3 (O), IC29.4 (I0), IC29.9 (I0), IC29.13 (I1)
+3V3: C134.2, C136.1, C139.2, C141.1, IC29.14 (VDD), IC30.5 (VDD), IC31.2 (VDD), IC32.8 (VDD), R151.1, R156.1, R159.1, X13.15, X15.15; also elsewhere on the board
+5V: FB7.P$1 (1); also elsewhere on the board
AUX1_USET_IN: X12.8, X12.8.1, X13.11, ZD11.C
AUX2_USET_IN: X14.8, X14.8.1, X15.11, ZD12.C
BATT_NTC: OK5.4 (COL), R151.2; also elsewhere on the board
CH1_GND: C132.2, C133.1, IC28.1 (GND), OK5.2 (C), X12.7, X12.7.1, ZD11.A; also elsewhere on the board
CH1_VDD: C132.1, IC27.1 (E), IC27.4 (E), IC28.4 (R), IC28.8 (V+); also elsewhere on the board
CH2_GND: X14.7, X14.7.1, ZD12.A; also elsewhere on the board
DOUT1: R166.1; also elsewhere on the board
DOUT2: IC29.5 (I1); also elsewhere on the board
ENC_A: C138.1, R165.1; also elsewhere on the board
ENC_B: C137.2, R157.1; also elsewhere on the board
ENC_SW: C135.2, SW2.D (1); also elsewhere on the board
EOUT_A: R159.2, R165.2, SW2.A
EOUT_B: R156.2, R157.2, SW2.B
EXT_TRIG: R164.1; also elsewhere on the board
GND: C134.1, C135.1, C136.2, C137.1, C138.2, C139.1, C140.1, C141.2, C156.2, D19.1 (A1), IC29.7 (VSS), IC30.3 (VSS), IC31.3 (GND), IC32.4 (VSS), OK5.3 (EMIT), OK6.2 (C), Q32.2 (S), Q33.2 (S), R154.2, R158.2, R178.2, SW2.C, SW2.E (S), SW2.GND1 (C), SW2.GND2 (C), SW3.1, SW3.2, SW3.5 (5-GND), X12.1, X12.1.1, ZD13.A; also elsewhere on the board
unnamed: F1.2, X14.2, X14.2.1
unnamed: IC27.2 (B), IC27.3 (C), IC27.5 (B), R177.2
unnamed: IC29.8 (O), Q32.1 (G), R154.1
unnamed: IC29.6 (O), X16.7
unnamed: C133.2, IC28.2 (TR), IC28.6 (THR), R153.2
unnamed: IC27.6 (C), IC28.7 (DIS), R152.1
unnamed: OK5.1 (A), R150.2
unnamed: D19.3 (C1A2), R162.1, R163.2
unnamed: IC30.2 (I), R163.1
unnamed: IC30.4 (O), R164.2
unnamed: R161.2, X12.2, X12.2.1
unnamed: D19.2 (C2), R155.1, ZD13.C
unnamed: D20.C, R155.2
unnamed: D20.A, FB7.P$2 (2)
unnamed: C156.1, IC31.4 (PFI), R160.2, R178.1
unnamed: D21.C, IC31.7 (!RESET)
unnamed: R161.1, R162.2
unnamed: R152.2, R153.1
unnamed: OK6.1 (A), R166.2
unnamed: IC29.2 (I1), IC31.5 (!PFO)
unnamed: F1.1, OK6.4 (COL), ZD14.C
unnamed: OK6.3 (EMIT), X14.1, X14.1.1, ZD14.A
NTC_IN: R177.1, X12.6, X12.6.1
PWRDIR: IC29.12 (I0); also elsewhere on the board
PWRSS: IC29.10 (I1); also elsewhere on the board
PWR_DIRECT: Q33.3 (D); also elsewhere on the board
PWR_EN: IC29.11 (O), Q33.1 (G), R158.1
PWR_SSTART: Q32.3 (D); also elsewhere on the board
SYNC1: IC32.3 (O); also elsewhere on the board
SYNC2: IC32.5 (I0), IC32.6 (I1), IC32.7 (O); also elsewhere on the board
SYNC_MASTER: IC32.1 (I0), IC32.2 (I1); also elsewhere on the board
TEMP_FREQ1: IC28.3 (Q), R150.1
WATCHDOG: IC31.6 (WDI); also elsewhere on the board

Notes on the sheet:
Channel 1 V/F converter for battery NTC (optional)
External trigger protection and level shifter/buffer
Remote programming inputs
Licensed under the TAPR Open Hardware License (www.tapr.org/OHL)
Repository: https://github.com/eez-open
More info at http://www.envox.hr/eez
Power-on reset generator and power control
Reset control, soft-start driver, encoder
V/F converter for battery NTC, External trigger
Master sync signal phase shifting
Rotary encoder
Opto-isolated digital output
DOUT2 driver
Encoder shaft length: 25 mm
Knob head: A3116068 (OKW), Knob cap: A3216007 (OKW)

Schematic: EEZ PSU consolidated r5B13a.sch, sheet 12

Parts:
C142, C143, C147, C148: 1n; C1206
C144: n.c; C1206
C145, C146: 2m2; ECAP7.5/18
C149: 1u; C0805
C150, C153: 470n; C0805
C151, C152: 4n7; C0805
C154: 100n; C0603
C155: 220n; C0805
D22, D23, D24, D25: STPS15H100; TO252
IC33: 74LVC1G125GW.125; SOT65P210X110-5N
IC34: TPA6205A1DGN; SOP65P490X110-9N
J7: 693072010801
R167: n.c.; R1206
R168: 12K; R1206
R169, R175: 20K; R0805
R170, R171: 1K; R0805
R172, R173: 10K; R0805
R174: 47K; R0805
SP2: LD-BZEN-0903
X19: 282836-2; TBLOCK5.0_2
X20: PCA-6B-20-HL-3 or 52746-2071; FPC-20_ROTATED
ZD15: n.c.; DO214AA
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

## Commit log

2015-11-09 Aux power r4B39 added
    [EEZ AUX PS r4B39 BOM.ods, EEZ AUX PS r4B39.brd, EEZ AUX PS r4B39.drills.xln, EEZ AUX PS r4B39.sch]
2015-11-10 mosfet post-regulator r4B44
    [EEZ PSU post-regulator r4B44 (SS).brd, EEZ PSU post-regulator r4B44 (SS).sch, EEZ PSU post-regulator r4B44.brd, EEZ PSU post-regulator r4B44.drills.xln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]
2015-11-10 mosfet pre-regulator r3B3b
    [EEZ Mosfet pre-regulator r3B3b (SS).brd, EEZ Mosfet pre-regulator r3B3b (SS).sch, EEZ Mosfet pre-regulator r3B3b BOM.ods, EEZ Mosfet pre-regulator r3B3b.brd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]
2015-11-14 replaced R7 Farnell code in the BOM
    [EEZ AUX PS r4B39 BOM.ods]
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2015-12-07 Arduino Shield r1B12b
    [EEZ Arduino shield r1B12b BOM.ods, EEZ Arduino shield r1B12b.brd, EEZ Arduino shield r1B12b.drills.xln, EEZ Arduino shield r1B12b.sch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]
2015-12-07 Arduino Shield without BP option folder name fixed
    [EEZ Arduino shield r1B12b BOM.ods, EEZ Arduino shield r1B12b.brd, EEZ Arduino shield r1B12b.drills.xln, EEZ Arduino shield r1B12b.sch]
2015-12-09 Small fix on bottom solder mask
    [EEZ PSU post-regulator r4B44 (SS).brd, EEZ PSU post-regulator r4B44.brd]
2016-01-01 PCB panel for dual channel PSU
    [PCB panel M1.brd, PCB panel M1.drills.xln]
2016-01-27 AUX PS upgraded to r4B40
    [EEZ AUX PS r4B39 BOM.ods, EEZ AUX PS r4B39.brd, EEZ AUX PS r4B40 BOM.ods, EEZ AUX PS r4B40.brd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]
2016-02-04 minor textual corrections
    [EEZ AUX PS r4B40 BOM.ods, EEZ Arduino shield r1B12b BOM.ods, EEZ Arduino shield+BP r1B12b BOM.ods, EEZ Mosfet pre-regulator r3B3b (SS).sch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]
2016-03-14 mechanical drawing
    [EEZ AUX PS r4B40.brd, EEZ PSU enclosure (Economica 320x200x115).brd, EEZ PSU enclosure (Economica 320x200x115).dxf]
2016-03-27 Arduino Shield r1B13, Post-regulator r45B45
    [AUX PS board side support (Economica 320x200x115).brd, AUX PS board side support (Economica 320x200x115).dxf, EEZ AUX PS r4B40.brd, EEZ Arduino shield+BP r1B12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]
2016-03-27 Arduino Shield r1B13 BOM updated
    [EEZ Arduino shield+BP r1B12c BOM.csv, EEZ Arduino shield+BP r1B12c BOM.ods, EEZ Arduino shield+BP r1B13 BOM.ods, EEZ Arduino shield+BP r1B13.brd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]
2016-03-27 light pipes added into Arduino Shield r1B13 BOM
    [EEZ Arduino shield+BP r1B13 BOM.ods]
2016-03-28 Few PCB layout correction for SMPS pre-regulator r1B1
    [EEZ SMPS pre-regulator r1B1.GBL, EEZ SMPS pre-regulator r1B1.GBS, EEZ SMPS pre-regulator r1B1.GKO, EEZ SMPS pre-regulator r1B1.GTL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]
2016-03-28 Updated Gerber files for Arduino Shield r1B13
    [EEZ Arduino shield+BP r1B13.GBL, EEZ Arduino shield+BP r1B13.GBS, EEZ Arduino shield+BP r1B13.GKO, EEZ Arduino shield+BP r1B13.GTL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]
2016-03-28 Arduino Shield r1B13a update
    [EEZ Arduino shield+BP r1B13.GTL, EEZ Arduino shield+BP r1B13a.GBL, EEZ Arduino shield+BP r1B13a.GBS, EEZ Arduino shield+BP r1B13a.GKO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]
2016-03-30 Power board r5B6b added
    [EEZ PSU power board r5B6b BOM.ods, EEZ PSU power board r5B6b.GBL, EEZ PSU power board r5B6b.GBS, EEZ PSU power board r5B6b.GKO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]
2016-03-30 Arduino shield+BP r2B6b (Due only) added
    [EEZ Arduino shield+BP r2B6b BOM.ods, EEZ Arduino shield+BP r2B6b.GBL, EEZ Arduino shield+BP r2B6b.GBS, EEZ Arduino shield+BP r2B6b.GKO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]
2016-03-30 AUX PS r5B6a added
    [EEZ AUX PS r5B6a BOM.ods, EEZ AUX PS r5B6a.GBL, EEZ AUX PS r5B6a.GBS, EEZ AUX PS r5B6a.GKO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]
2016-03-30 mechanical drawing added
    [EEZ PSU Galaxy 230x80 panels.brd, EEZ PSU Galaxy 230x80 panels.dxf]
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2016-04-07 Replaced IEC inlet in preliminary rev5
    [EEZ AUX PS r5B6a BOM.ods, EEZ PSU Galaxy 230x80 panels r2.brd, EEZ PSU Galaxy 230x80 panels r2.dxf, EEZ PSU Galaxy 230x80 panels.dxf]
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2016-04-17 SMPS pre-regulator small corrections
    [EEZ PSU post-regulator r4B45.sch, EEZ PSU power board r5B6b BOM.ods, EEZ SMPS pre-regulator r1B1.brd, EEZ SMPS pre-regulator r1B1.sch]
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2016-05-26 AUX PS r4B3, various BOM corrections
    [EEZ AUX PS r4B42 BOM.ods, EEZ AUX PS r4B43 BOM.ods, EEZ AUX PS r4B43.GBL, EEZ AUX PS r4B43.GBS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]
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2016-06-16 Power board tiny text corrections
    [EEZ PSU power board r5B8.sch]
2016-06-17 Power board gerber files text correction
    [EEZ AUX PS r5B8.GBL, EEZ AUX PS r5B8.GBO, EEZ AUX PS r5B8.GBS, EEZ AUX PS r5B8.GKO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]
2016-06-17 Power board and AUX PS gerber files correction
    [EEZ AUX PS r5B8.GBL, EEZ AUX PS r5B8.GBO, EEZ AUX PS r5B8.GBS, EEZ AUX PS r5B8.GKO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]
2016-06-17 Screen masks correction
    [EEZ AUX PS r5B8.GTO, EEZ AUX PS r5B8.brd, EEZ Arduino shield+BP r3B3.GBL, EEZ Arduino shield+BP r3B3.GBO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]
2016-06-17 Arduino Shield BOM correction
    [EEZ PSU Arduino shield+BP r3B3 BOM.ods]
2016-06-17 Arduino Shield correction
    [EEZ Arduino shield+BP r3B3.GBL, EEZ Arduino shield+BP r3B3.GBS, EEZ Arduino shield+BP r3B3.GTL, EEZ Arduino shield+BP r3B3.GTO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]
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2016-06-18 Power board R28, R29 PCB layout, BOM corrections
    [EEZ PSU Arduino shield+BP r3B3 BOM.ods, EEZ PSU power board r5B8 BOM.ods, EEZ PSU power board r5B8.GBL, EEZ PSU power board r5B8.GTL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]
2016-06-18 Small BOM corrections
    [EEZ PSU AUX PS r5B8 BOM.ods, EEZ PSU Arduino shield+BP r3B3 BOM.ods, EEZ PSU power board r5B8 BOM.ods]
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2016-06-19 Enclosure corrections
    [EEZ PSU H24005 enclosure.brd, EEZ PSU H24005 enclosure.dxf]
2016-06-19 Arduino shield D5 PCB layout, BOM corrections
    [EEZ Arduino shield+BP r3B3.GBL, EEZ Arduino shield+BP r3B3.GTL, EEZ Arduino shield+BP r3B3.GTO, EEZ Arduino shield+BP r3B3.GTS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]
2016-06-19 Rt value corrections for AUX PS and Power board
    [EEZ AUX PS r5B8.GTO, EEZ AUX PS r5B8.brd, EEZ AUX PS r5B8.sch, EEZ PSU AUX PS r5B8 BOM.ods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]
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2016-06-25 Fixed fan control, miniMELF replaced with SOD-323
    [EEZ PSU consolidated r5B8.brd, EEZ PSU consolidated r5B8.sch, EEZ PSU r5B8 panel.GBL, EEZ PSU r5B8 panel.GBO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]
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2016-07-25 small correction on Arduino shield PCB silkscreens
    [EEZ Arduino shield+BP r3B4.GBL, EEZ Arduino shield+BP r3B4.GBO, EEZ Arduino shield+BP r3B4.GBS, EEZ Arduino shield+BP r3B4.GKO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]
2016-07-25 BOM corrections, Q1 gate trace improved
    [EEZ PSU consolidated r5B9 BOM.ods, EEZ PSU consolidated r5B9.brd, EEZ PSU power board r5B9.GBL, EEZ PSU power board r5B9.GBO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]
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2016-07-28 Small corrections on top silkscreen
    [EEZ PSU AUX PS r5B9.GBL, EEZ PSU AUX PS r5B9.GTL, EEZ PSU AUX PS r5B9.XLN, EEZ PSU AUX PS r5B9.brd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]
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2016-08-12 corrected acryl enclosure drawings
    [EEZ PSU H24005 enclosure r4.5 (for 4mm acryl).dxf, EEZ PSU H24005 enclosure r4.5a (for 4mm acryl).dxf]
2016-08-15 binding post holes corrected
    [EEZ PSU H24005 enclosure r4.6 (for 4mm acryl).dxf, EEZ PSU H24005 enclosure r4.6.brd, EEZ PSU H24005 enclosure r4.6.dxf]
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2016-09-04 R97 and R102 values swapped
    [EEZ PSU consolidated r5B9 BOM.ods, EEZ PSU consolidated r5B9.brd, EEZ PSU consolidated r5B9.sch, EEZ PSU power board r5B9 BOM.ods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]
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2016-09-06 BOM Farnell parts corrected, reformated for printing
    [EEZ PSU consolidated r5B9 BOM.ods]
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2016-09-29 Changed wrong designators in schematics on page 3, 6 and 8
    [EEZ PSU consolidated r5B9.sch]
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2016-10-25 r5B10 BOM, top silkscreen minor correction
    [EEZ PSU consolidated r5B10+wire harness BOM.ods, EEZ PSU consolidated r5B10.brd, EEZ PSU consolidated r5B10.sch, EEZ PSU consolidated r5B9+wire harness BOM.ods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]
2016-10-25 r5B10 bottom silkscreen minor correction
    [EEZ PSU r5B10 panel.GBO]
2016-10-25 r5B10 bottom silkscreen another minor correction
    [EEZ PSU consolidated r5B10.brd, EEZ PSU r5B10 panel.GBO, EEZ PSU r5B10 panel.brd]
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2016-11-30 #13 BOM correction
    [EEZ PSU consolidated r5B10+wire harness BOM.ods]
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2016-12-14 BOM estimated total corrected
    [EEZ PSU consolidated r5B11 BOM.ods]
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2017-01-11 Corrections on bottom silkscreen
    [EEZ PSU consolidated r5B11.brd, EEZ PSU r5B11 panel.GBL, EEZ PSU r5B11 panel.GBO, EEZ PSU r5B11 panel.GBS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]
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2017-03-11 Q24-> mosfet, swap outputs of Q32, Q33
    [EEZ PSU consolidated r5B12 BOM.ods, EEZ PSU consolidated r5B12.brd, EEZ PSU consolidated r5B12.sch, EEZ PSU r5B12 panel.GBL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]
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2017-03-13 X14 pin 1, 2 swap, R177
    [EEZ PSU consolidated r5B12 BOM.ods, EEZ PSU consolidated r5B12.brd, EEZ PSU consolidated r5B12.sch, EEZ PSU r5B12 panel.GBL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]
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2017-03-15 wire harness corrections
    [EEZ PSU consolidated r5B12.sch]
2017-03-16 IC29 package size fixed in BOM
    [EEZ PSU consolidated r5B12 BOM.ods]
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2017-04-17 SKL16 diode package fix
    [EEZ PSU consolidated r5B12 BOM.ods, EEZ PSU consolidated r5B12.sch]
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2017-07-09 IC22 package fix
    [EEZ PSU consolidated r5B12 BOM.ods, EEZ PSU consolidated r5B12.brd, EEZ PSU consolidated r5B12.sch]
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2018-09-02 Created netlist, and updated PCB
    Updated PCB to only use footprints only in the local footprint library
    Fixed DRC errors on schematic
    Generated netlist and corrected errors
    [AC_soft-start,_+5V_power.sch, Bias_power.sch, Binding_posts_relays,_LED_driver.sch, CC%2fCV,_Remote_sense_protection.sch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]
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2018-09-02 Modified PCB file
    My repairs left a trace dangling where it shouldn't have, corrected.
    [EEZ PSU consolidated r5B13a.kicad_pcb]
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

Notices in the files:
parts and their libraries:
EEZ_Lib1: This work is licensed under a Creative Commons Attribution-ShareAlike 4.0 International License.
